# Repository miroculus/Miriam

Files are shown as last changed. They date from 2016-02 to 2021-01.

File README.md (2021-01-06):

Miriam
========

**🆕📻⚠️ IMPORTANT: A more updated repository which fixes several critical bugs is at https://github.com/strawlab/Miriam .**



Copyright Miroculus Inc.2016
Based on original work from Arduino (Sweden)

This documentation describes Open Hardware and is licensed under the CERN OHL v. 1.2.

Licensed under CERN OHL v.1.2

You may redistribute and modify this documentation under the terms of the [CERN OHL v.1.2.](http://ohwr.org/cernohl). This documentation is distributed WITHOUT ANY EXPRESS OR IMPLIED WARRANTY, INCLUDING OF MERCHANTABILITY, SATISFACTORY QUALITY AND FITNESS FOR A PARTICULAR PURPOSE. Please see the CERN OHL v.1.2 for applicable conditions

## Introduction

Miriam is an open-source instrument for isothermal amplification reactions. The assays Miriam was designed to execute are based on LAMP and Elisa protocols. Miriam is controlled with [Arduino](http://www.arduino.cc/) Mega and the production costs per instrument are blow 200USD.

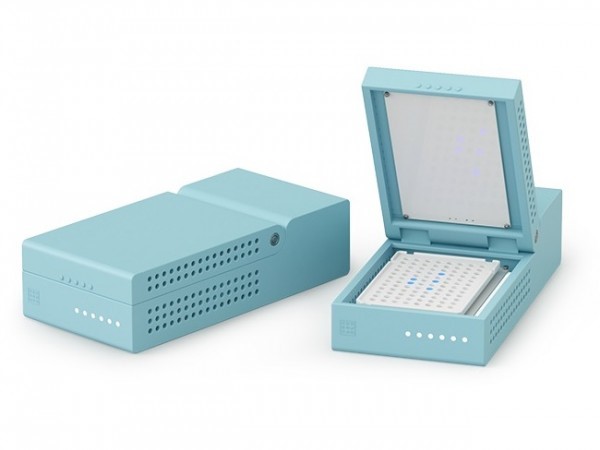
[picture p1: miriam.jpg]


The detection optics have been designed for [calcein dye](http://loopamp.eiken.co.jp/e/products/fluore/index.html). The selected LED is an angle SMD led with peak wavelength 461nm. The photodiode is an RGB photodiode most sensitive to green light. The optics also include an emission filter utilized in theatrical lighting.  The development and selection of components is further described in a [Master's thesis](http://lutpub.lut.fi/handle/10024/159386) done from miriam. 

In the performance testing of Miriam, the detection limit for DNA using LAMP as amplification platform has been 2amol in 10ul of sample (figure 1).

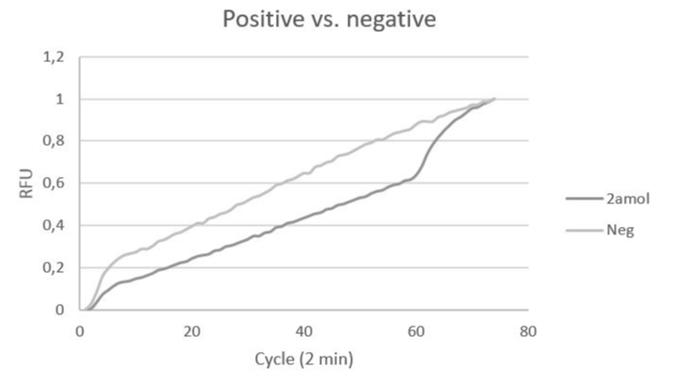
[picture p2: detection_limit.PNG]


**Figure 1.** LAMP reaction with 2amol DNA input, fluorescence measured every 2 minutes (y, Normalized signal and x, cycle (2 min).

For more information, you can contact us by completing the form [here](https://miroculus.com/#contact). You can also follow Miroculus on [twitter](https://twitter.com/miroculus) or like us on [facebook](https://www.facebook.com/miroculus).

To report a *bug* in the software or to request *a simple enhancement* go to the [issues](http://github.com/miroculus/Miriam/issues) section

If you're interested in modifying or extending the Miriam platform, we strongly suggest you to send us an email discussing your ideas. That way you can coordinate with our team and others, giving your work a higher chance of being integrated into the official release.

## Design

The optics of Miriam are designed to support calcein dye. Calcein emission and excitation spectra are represented in Figure 2.

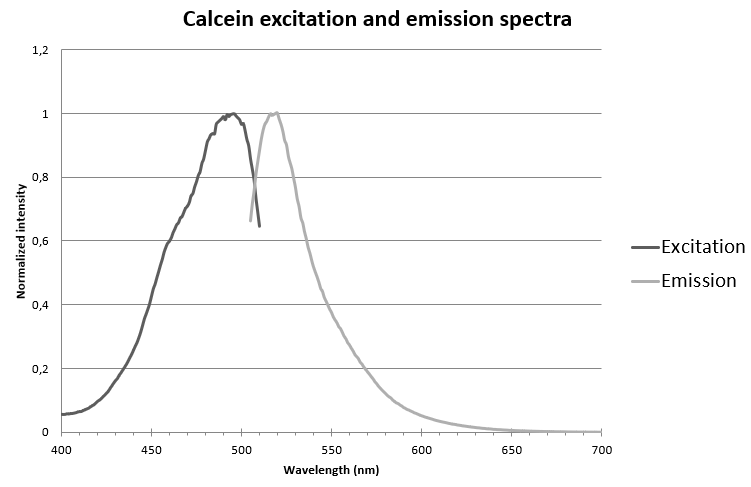
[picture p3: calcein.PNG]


**Figure 2.** Calcein normalized emission and excitation spectra.

The optical filter for blocking the excitation light has been purchased from a theatrical supply store and has the transmission spectra represented in Figure 3.

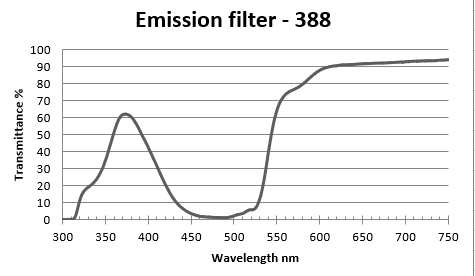
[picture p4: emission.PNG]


**Figure 3.** Emission filter transmission specter.

The middle heating board and the LED and PD arrangements have been designed to support 96-well plates with the following dimensions (figure 4).

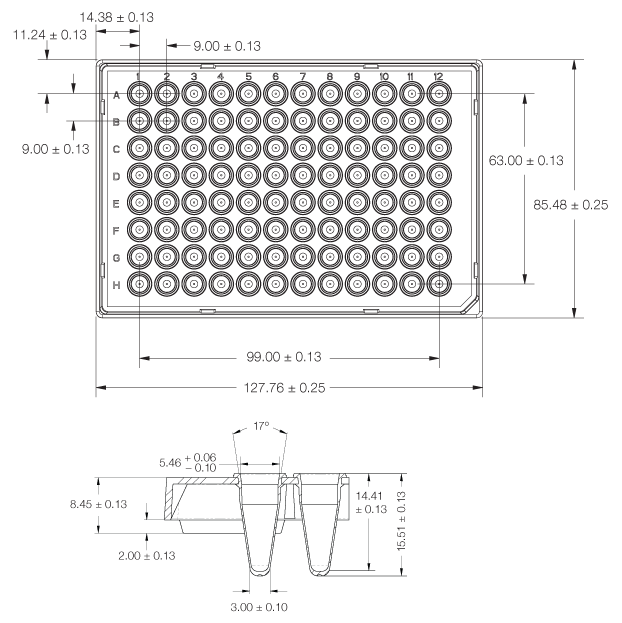
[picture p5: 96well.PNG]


**Figure 4.** 96-well plate dimensions supported by Miriam

To control the heating of Miriam there are two heater PCBs. They have been designed so that in the middle is a 10 kohm SMD thermistor and the heat is generated by current flowing through the copper traces. These traces have been designed to be so long and narrow that they create an internal resistance of few ohms. The traces are closer to each other in the edges because heat is measured from the middle and the edges of the PCB boards meet ambient air and they need to produce more heat. (Figure 5.)

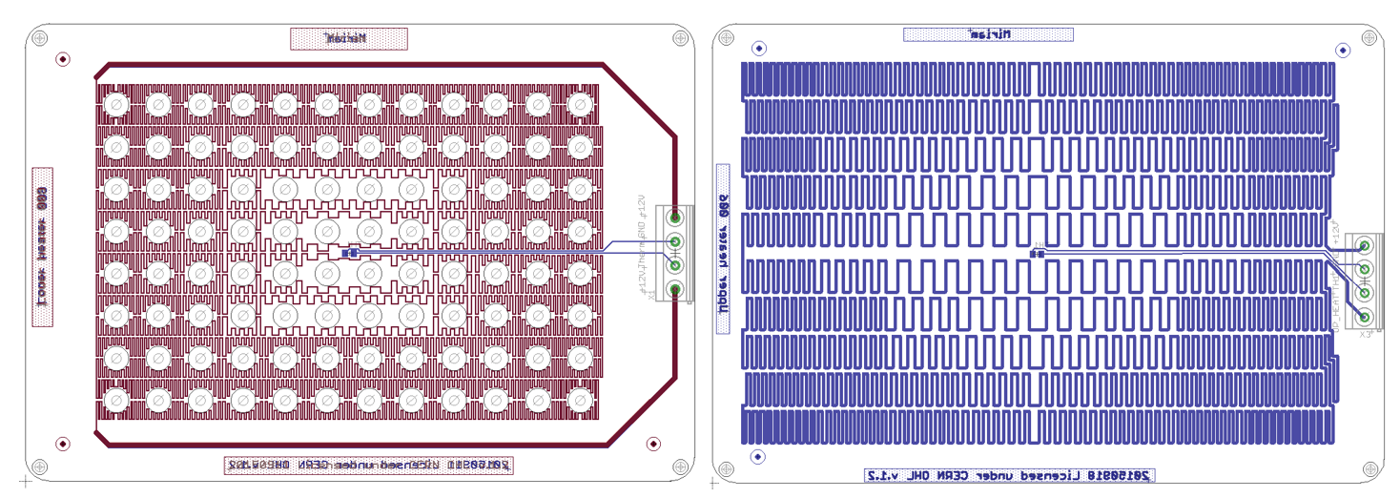
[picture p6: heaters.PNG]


**Figure 5.** Heating plates, heat is generated by trace resistance. Right: The middle heater creating the temperature required for amplification (58-68 degrees C). Left: The top heater keeping vapor from condensing to the lid, kept at 80 degrees C. 

The detection of fluorescence is done with 96 LEDs and 96 photodiodes creating LED and photodiode PCBs. The LED peak wavelength is 470 nm and photodiode is a green RGB photodiode. The measured voltage is amplified with an operational amplifier to 0-5 V that is then converted by Arduino’s 8-bit ADC to be a numerical value. (figure 6.)

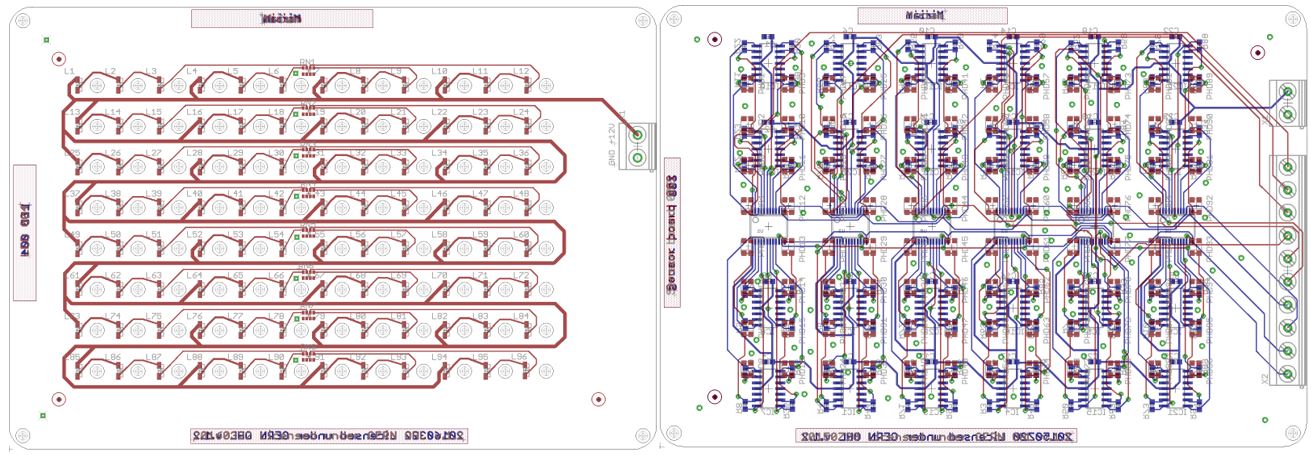
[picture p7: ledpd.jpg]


**Figure 6.** LED (left) and photodiode (right) PCBs.

All of these boards are controlled by a shield that is directly mounted to the Arduino mega board (figure 7). The shield contains three MOSFETs to control LED board and the two heater boards, the required components to read the heat from the thermistors as well as a WIFI chip. The WIFI chip makes it possible for Arduino to be connected to a local WIFI and this way communicate autonomously to a web service.

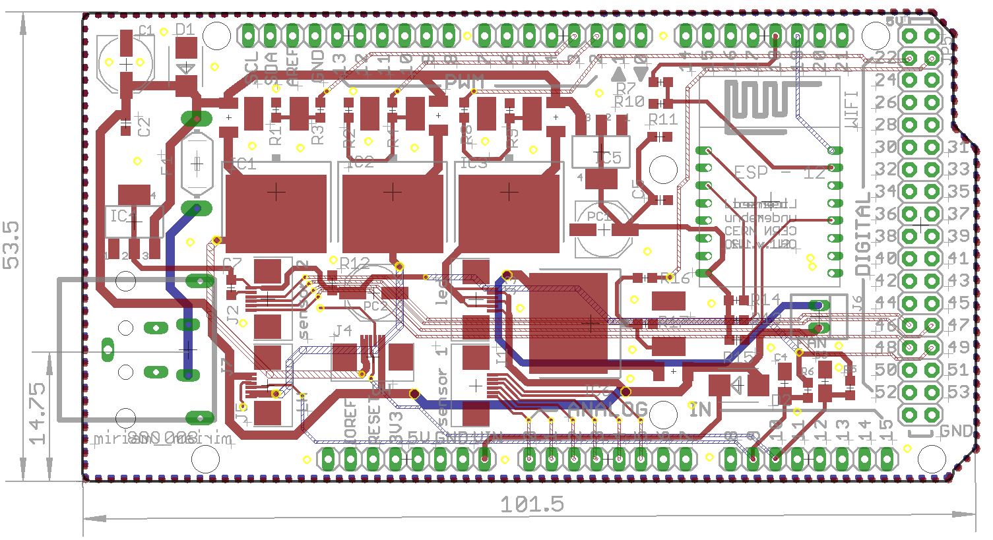
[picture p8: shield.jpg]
shield


**Figure 7.** The Arduino shield. The power connector is a 20-pin ATX connector that can be connected to a computer ATX power.

Installation
------------
3D print the printable parts under folder "3D model", sand them to make them align with each other. Assemble the boards as presented in the Figure 8. In the assembly cut with scissors the emission filter to fit between the LED and the sensor PCBs so that it aligns with the bolts.

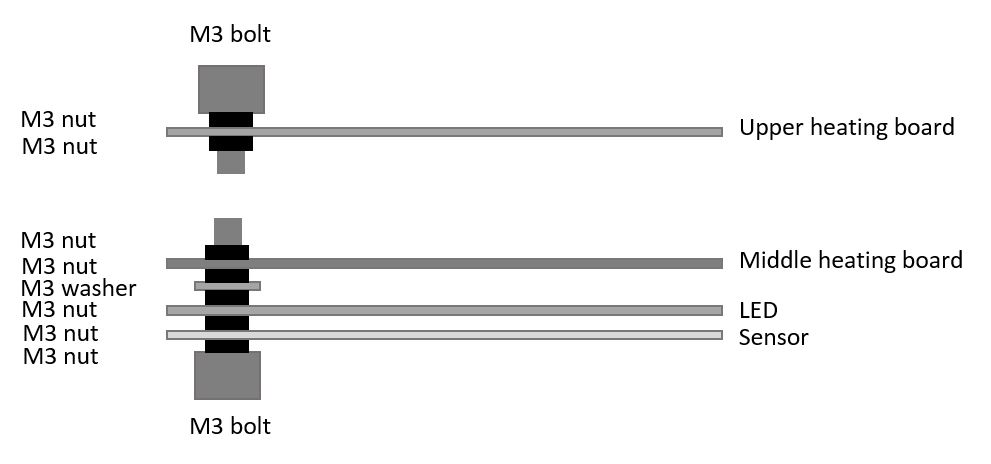
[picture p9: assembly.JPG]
screws


**Figure 8.** PCB board assembly information.

The screws are attached to the cover and the base with heat durable epoxy. 

Credits
--------
Miriam is an open source project, supported by Miroculus in collaboration with Arduino (Sweden). The team is led by Juho Terrijarvi.

Icon and image designed by Miroculus.

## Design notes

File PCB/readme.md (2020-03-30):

# PCBs

The PCBs have been drawn with Eagle software 7.3.0

PCB order details are in separate readme files in correct subfolders.

The Bills of material can be found under folder BOM. Datasheets of the main components are under folder Components.

Some of the component layouts can be found under Library folder that houses the Eagle .lbrs

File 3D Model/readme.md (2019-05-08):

# 3D printable parts

Miriam is composed of 3 pieces that can be 3D printed.

## base.stl

Base is where the mid heating and optic PCBs are located and where the plate to run the assay comes to. It also houses the Arduino Mega and its control shield in the back of the case. 

The outer dimensions of the base are 275 x 132 x 75 mm.

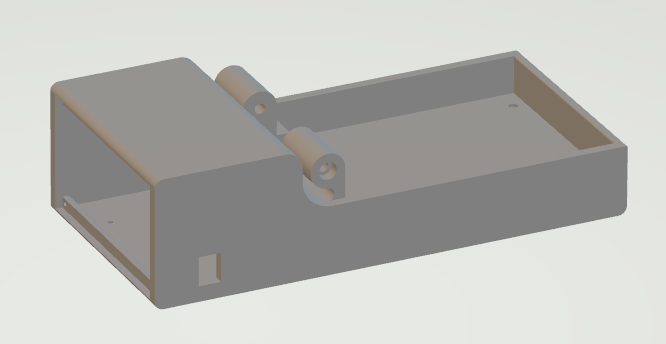
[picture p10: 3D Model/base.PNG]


## upper.stl 

This is the cover of the case that houses the upper heating board. The outer dimensions are 191 x 132 x 35 mm.

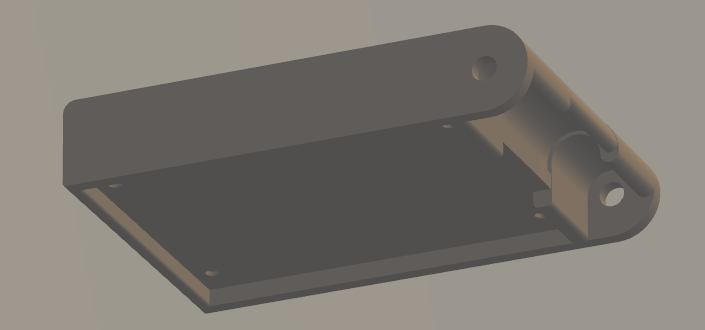
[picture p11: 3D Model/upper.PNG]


## cover.stl

Cover is meant to hide the Arduino mega and shield in the back of the case. The dimensions are 6 x 120 x 67 mm.

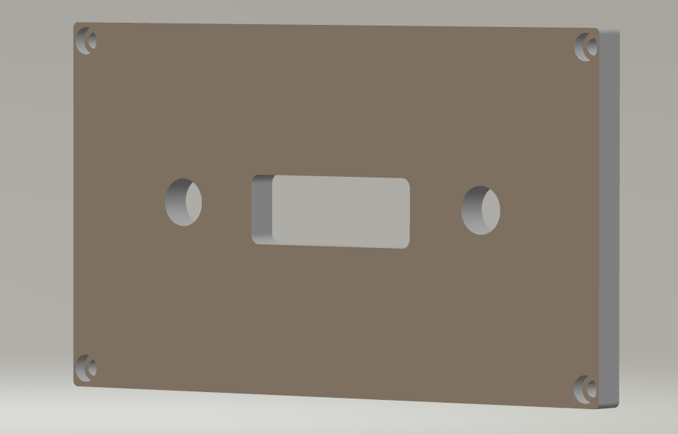
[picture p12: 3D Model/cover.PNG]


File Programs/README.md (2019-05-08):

Miriam SW/FW
========

(c) 2016 Juho Terrijarvi juho@miroculus.com, Miroculus Inc.

(c) 2014 Juanjo Tara j.tara@arduino.cc, Arduino Verkstad AB (For FWs)

These programs are free software: you can redistribute them and/or modify them under the terms of the GNU General Public License as published by the Free Software Foundation, either version 3 of the License, or (at your option) any later version.

These programs are distributed in the hope that they will be useful, but WITHOUT ANY WARRANTY; without even the implied warranty of MERCHANTABILITY or FITNESS FOR A PARTICULAR PURPOSE.  See the GNU General Public License for more details.

You should have received a copy of the GNU General Public License along with this program.  If not, see <http://www.gnu.org/licenses/>.

## Programs

Firmware is written with [Arduino IDE](https://www.arduino.cc/en/main/software) and the software with Visual Studio 2015 open community using C#.

* Serial_003 is meant for communication between computer and Miriam via USB cable and string messages
* Wifi_003 is for interaction between controller and Miriam over the same wifi network
* Wifi_004 webservice controls Miriam

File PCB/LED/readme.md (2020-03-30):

# LED_005

- material: FR4
- Single sided assembly
- 1oz copper
- 1.6 mm thick
- Leadfree HAL
- Black soldermask
- White silkscreen

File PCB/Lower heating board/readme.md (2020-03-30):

# LH_010

- material aluminum
- 2 layer
- single sided assembly
- 1oz copper
- 1.6 mm thick
- Leadfree HAL
- Black soldermask
- White silkscreen

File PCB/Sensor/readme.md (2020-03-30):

# Sensor_002

- material FR4
- 2 layer
- double sided assembly
- 1oz copper
- 1.6 mm thick
- Leadfree HAL
- Black soldermask
- White silkscreen

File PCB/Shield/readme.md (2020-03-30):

# shield_008

- material FR4
- 4 layers
- 1oz copper
- 1.6 mm thick
- Leadfree HAL
- Black soldermask
- White silkscreen
- Pay attention to milling layer GML
- One sided assembly

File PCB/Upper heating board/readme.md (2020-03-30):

# UH_007

- 2 layer PCB
- One sided assembly
- material FR4
- 1oz copper
- 1.6 mm thick
- Leadfree HAL
- Black soldermask
- White silkscreen

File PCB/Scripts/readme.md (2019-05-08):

# Scripts

This folder has the outer dimensions of each PCB. Script template.csv is an example script to draw the traces for the heating boards. It was easiest to calculate the lengths of each wire in Excel.

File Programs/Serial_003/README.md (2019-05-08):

Serial_003
========

This SW / FW combination is meant for serial communication between a computer and Miriam. Miriam is connected with a USB cable to the controlling computer and messaging between the two happen via string messages over RX/TX protocol.
- SW 'R' (read assay) - FW 'A1,A2,A3...E12'
- SW 'i' (info) - FW 'outputMiddle, outputUpper, temperatureMiddle, temperatureUpper, temperatureMiddleC, temperatureUpperC'
- SW 'U param' (upper wanted temperature, i.e. U 80) - FW 'temperatureUpperSet'
- SW 'M param' (middle wanted temperature, i.e. M 63) - FW 'temperatureMiddleSet'
- SW 'C' (cancel, turn off the heat) - FW 'Cancel'

Once the temperature has been set, the actual temperature needs to be refreshed by clicking 'Ask heat'. The assay, once started, can always be turned off simply by closing the program. The assay results are saved to the desktop in a .csv file.

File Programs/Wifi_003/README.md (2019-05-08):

Wifi_003
========

This SW / FW combination is meant for communication over the same WIFI connection between a computer and Miriam. Miriam is first connected with a USB cable to the controlling computer and the WIFI details are given to Miriam and the IP address when connected read. Messaging between the two happen via string messages in http format.
- SW 'R' (read assay) - FW 'A1,A2,A3...E12'
- SW 'i' (info) - FW 'outputMiddle, outputUpper, temperatureMiddle, temperatureUpper, temperatureMiddleC, temperatureUpperC'
- SW 'U param' (upper wanted temperature, i.e. U 80) - FW 'temperatureUpperSet'
- SW 'M param' (middle wanted temperature, i.e. M 63) - FW 'temperatureMiddleSet'
- SW 'C' (cancel, turn off the heat) - FW 'Cancel'

Once the temperature has been set, the actual temperature needs to be refreshed by clicking 'Ask heat'. The assay, once started, can always be turned off simply by closing the program. The assay results are saved to the desktop in a .csv file.

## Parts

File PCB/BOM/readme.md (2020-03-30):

# Components

Components required for the PCB assembly are listed in the BOMs. Main components contain a link to the component. Datasheets can be found under ./Components.

The emission filter is purchased from a Swedish theatrical supply store. The transmission spectrum of the [GAM-388](http://shop.hofmann.se/GAM_Orange_gold_rush_filter?id=388-GAM#.VaYDufktM9s) filter is represented in the main readme. To even out the distribution of heat an [elastic heat pressure surface](http://catalog.cshyde.com/item/all-categories/solid-silicone-thermally-conductive-/71-tcd-60d-0625) can be used between the 96-well plate and the upper heating board.

List of the components can also be found from [joint bom](List of components required can be found: https://docs.google.com/spreadsheets/d/1FHOCzn1yYIiR1e6U7Qw9gCIf-KbuHXV_sOKSGwqRR3c/edit?usp=sharing) where also a possible power supply is listed.

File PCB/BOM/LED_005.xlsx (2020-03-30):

PCB: | LED_003
part | pcs/pcb | Value | Package | Description | Remark | Link
RN1,RN2,RN3,RN4,RN5,RN6,RN7,RN8 | 8 | 181 | CAY16 | Array Chip Resistor | 4R-NCAY16 | http://www.digikey.hk/product-detail/en/bourns-inc/CAT16-181J4LF/CAT16-181J4LFCT-ND/3592895
FD1,FD2,FD3 | 3 | FIDUCIALMOUNT | FIDUCIA-MOUNT | FIDUCIALMOUNT
L1,L2,L3,L4,L5,L6,L7,L8,L9,L10,L11,L12,L13,L14,L15,L16,L17,L18,L19,L20,L21,L22,L23,L24,L25,L26,L27,L28,L29,L30,L31,L32,L33,L34,L35,L36,L37,L38,L39,L40,L41,L42,L43,L44,L45,L46,L47,L48,L49,L50,L51,L52,L53,L54,L55,L56,L57,L58,L59,L60,L61,L62,L63,L64,L65,L66,L67,L68,L69,L70,L71,L72,L73,L74,L75,L76,L77,L78,L79,L80,L81,L82,L83,L84,L85,L86,L87,L88,L89,L90,L91,L92,L93,L94,L95,L96 | 96 | KA-2810AQBS-G | LED_0.2 | LED_0.2 | LED | http://www.newark.com/kingbright/ka-2810aqbs-g/led-blue-2-8-x-0-8mm-300mcd-465nm/dp/28W1790?ost=KA-2810AQBS-G
J1 | 1 |  | 68710614522 | WE-FPC 0.5mm SMT ZIF Horizontal Bottom Contact, 6 Pins=>Code : Con_FPC_ZIF_0.50_68710614522 |  | https://www.digikey.fi/product-detail/en/wurth-electronics-inc/68710614522/732-2010-1-ND/2060634

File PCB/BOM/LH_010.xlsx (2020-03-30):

PCB: | LH_010
part | pcs/pcb | Value | Package | Description | Remark
J1 | 1 |  | 68710614522 | WE-FPC 0.5mm SMT ZIF Horizontal Bottom Contact, 6 Pins=>Code : Con_FPC_ZIF_0.50_68710614522 |  | https://www.digikey.fi/product-detail/en/wurth-electronics-inc/68710614522/732-2010-1-ND/2060634
TH1 | 1 | 10K | THERMISTOR_SMD_0603 | THERMISTOR_SMD_0603 | NTC

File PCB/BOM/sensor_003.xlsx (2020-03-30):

PCB: | sensor_002
part | pcs/pcb | Value | Package | Description | Remark | Link
C1,C2,C3,C4,C5,C6,C7,C8,C9,C10,C11,C12,C13,C14,C15,C16,C17,C18,C19,C20,C21,C22,C23,C25 | 24 | 100nF | C0603 | C-EUC0603 | CAPACITOR, European symbol
R1,R2,R3,R4,R5,R7,R8,R9,R10,R11,R12,R13,R14,R15,R16,R17,R18,R19,R20,R21,R22,R23,R24,R25,R26,R27,R28,R29,R30,R31,R32,R33,R34,R35,R36,R37,R38,R39,R40,R41,R42,R43,R44,R45,R46,R47,R48,R49,R50,R51,R52,R53,R54,R55,R56,R57,R58,R59,R60,R61,R62,R63,R64,R65,R66,R67,R68,R69,R70,R71,R72,R73,R74,R75,R76,R77,R78,R79,R80,R81,R82,R83,R84,R85,R86,R87,R88,R89,R90,R91,R92,R93,R94,R95,R96,R97 | 96 | 3.9Mohm | R0603 | R-EU_R0603 | RESISTOR, European symbol
U1,U2,U3,U4,U5,U6 | 6 | 74HC4067 | SSOP24 | MUX-1X16 | 1x16 Channel Analog Multiplexer/Demultiplexer [Part No.] | http://www2.mouser.com/ProductDetail/Texas-Instruments/CD74HC4067SM96G4/
PHD1,PHD2,PHD3,PHD4,PHD5,PHD6,PHD7,PHD8,PHD9,PHD10,PHD11,PHD12,PHD13,PHD14,PHD15,PHD16,PHD17,PHD18,PHD19,PHD20,PHD21,PHD22,PHD23,PHD24,PHD25,PHD26,PHD27,PHD28,PHD29,PHD30,PHD31,PHD32,PHD33,PHD34,PHD35,PHD36,PHD37,PHD38,PHD39,PHD40,PHD41,PHD42,PHD43,PHD44,PHD45,PHD46,PHD47,PHD48,PHD49,PHD50,PHD51,PHD52,PHD53,PHD54,PHD55,PHD56,PHD57,PHD58,PHD59,PHD60,PHD61,PHD62,PHD63,PHD64,PHD65,PHD66,PHD67,PHD68,PHD69,PHD70,PHD71,PHD72,PHD73,PHD74,PHD75,PHD76,PHD77,PHD78,PHD79,PHD80,PHD81,PHD82,PHD83,PHD84,PHD85,PHD86,PHD87,PHD88,PHD89,PHD90,PHD91,PHD92,PHD93,PHD94,PHD95,PHD96 | 96 | CLS15-22C/L213G/TR8 | PD_0.2 | PD_0.2 | Photodiode | http://www2.mouser.com/ProductDetail/Everlight/CLS15-22C-L213G-TR8/
FD1,FD2,FD3,FD4,FD5,FD6 | 6 | FIDUCIALMOUNT | FIDUCIALMOUNT | FIDUCIA-MOUNT
IC1,IC2,IC3,IC4,IC5,IC6,IC7,IC8,IC9,IC10,IC11,IC12,IC13,IC14,IC15,IC16,IC17,IC18,IC19,IC20,IC21,IC22,IC23,IC24 | 24 | LMV324 | SO14 |  | OP AMP | http://www2.mouser.com/ProductDetail/STMicroelectronics/LMV324LIDT/?qs=sGAEpiMZZMtCHixnSjNA6A1cCp3RWdULNBEJMAycdn8%3d
J1, J2 | 2 |  | 68710614522 | WE-FPC 0.5mm SMT ZIF Horizontal Bottom Contact, 6 Pins=>Code : Con_FPC_ZIF_0.50_68710614522 |  | https://www.digikey.fi/product-detail/en/wurth-electronics-inc/68710614522/732-2010-1-ND/2060634

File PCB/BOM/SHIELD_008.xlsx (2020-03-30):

PCB: | SHIELD_008
part | pcs/pcb | Value | Package | Description | Remark | Link
R7 | 1 | 1.69k | R0603 | RESISTOR, European symbol
R3, R4, R8, R16 | 4 | 100R | R0603 | RESISTOR, European symbol
C2, C5, C7 | 3 | 100n | C0603 | CAPACITOR, European symbol
R1, R2, R5, R6, R9, R13, R14, R15, R17 | 9 | 10K | R0603 | RESISTOR, European symbol
C3, C4 | 2 | 10u | A/3216-18R | POLARIZED CAPACITOR, European symbol |  | http://www2.mouser.com/ProductDetail/AVX/TPSA106K010R0900/?qs=YMBIwoNQYdV0MtGvKI9mmw%3D%3D
JP7 | 1 | 10x1F-H8.5 | 1X10 | PIN HEADER
JP5 | 1 | 18x2F-H8.5 | 2X18 | PIN HEADER
J6 | 1 | 22-23-2021 | 22-23-2021 | .100 (2.54mm) Center Header - 2 Pin"
R10 | 1 | 3.3k | R0603 | RESISTOR, European symbol
R11, R12 | 2 | 4.12k | R0603 | RESISTOR, European symbol
C1, PC1, PC2 | 3 | 47u | PANASONIC_D | POLARIZED CAPACITOR, European symbol |  | http://www.digikey.com/product-search/en?KeyWords=493-2086-1-ND&WT.z_header=search_go
JP1, JP2, JP3, JP4, JP6 | 5 | 8x1F-H8.5 | 1X08 | PIN HEADER
IC1, IC2, IC3, IC6 | 4 | FDB8880 | FDB8880 | FDB8880 N-Channel PowerTrench MOSFET |  | http://www2.mouser.com/ProductDetail/Fairchild-Semiconductor/FDB8880/
WIFI | 1 | ESP12 | ESP12 | ESP8266 Wifi module 12 |  | https://www.amazon.com/gp/aw/d/B00RJJHWLA/ref=ya_aw_od_pi?ie=UTF8&psc=1
D1, D2 | 2 | M7 | SMB | DIODE |  | http://www.digikey.com/product-detail/en/S1AB-13-F/S1AB-FDICT-ND/755488
F1 | 1 | MF-R1100 | LITTLEFUSE | LITTLEFUSE |  | http://www.digikey.com/product-search/en?KeyWords=MF-R1100-ND&WT.z_header=search_go
IC4 | 1 | NCV1117ST50T3GOSCT-ND | SOT223 | Adjustable Output Low Dropout Voltage Regulator 800 mA |  | http://www.digikey.com/product-detail/en/NCV1117ST50T3G/NCV1117ST50T3GOSCT-ND/1967231
IC5 | 1 | NCV1117ST33T3GOSCT-ND |  | Adjustable Output Low Dropout Voltage Regulator 800 mA |  | http://www.digikey.com/product-detail/en/NCV1117ST33T3G/NCV1117ST33T3GOSCT-ND/2705186
D3, D4, D5, D6 | 4 | RGL34A | DO-213AA_DIODE | RGL34A thru RGL34K |  | http://www.digikey.com/product-search/en?keywords=RGL34G-E3%2F98GICT-ND
J7 | 1 | KPJX-4S-S | KPJX-4S-S | 4 _Power_ Position Circular Connector Jack, Female Sockets Solder |  | https://www.digikey.fi/product-detail/en/kycon-inc/KPJX-4S-S/2092-KPJX-4S-S-ND/9990088
J1, J2, J3, J4, J5 | 5 |  | 68710614522 | WE-FPC 0.5mm SMT ZIF Horizontal Bottom Contact, 6 Pins=>Code : Con_FPC_ZIF_0.50_68710614522 |  | https://www.digikey.fi/product-detail/en/wurth-electronics-inc/68710614522/732-2010-1-ND/2060634

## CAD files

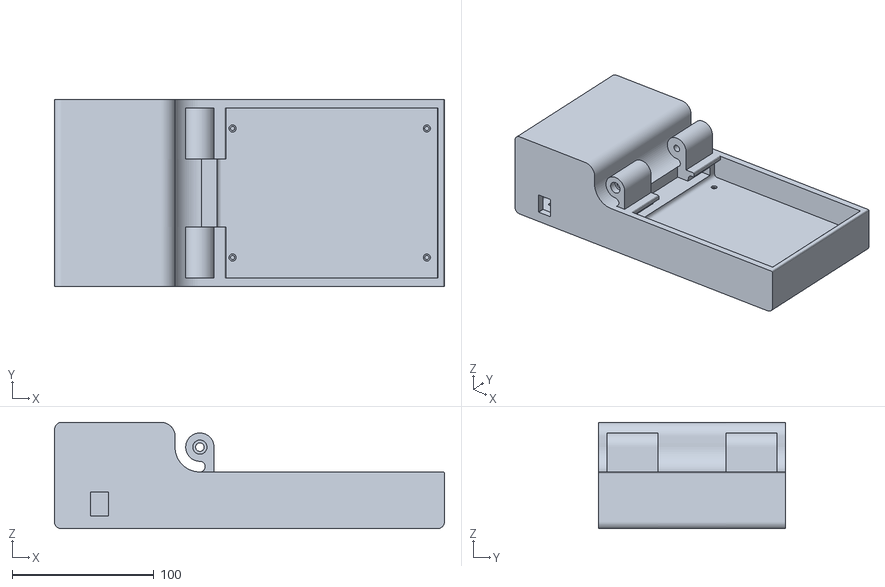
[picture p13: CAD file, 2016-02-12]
3D Model/base.stl
275.0 x 132.0 x 75.0

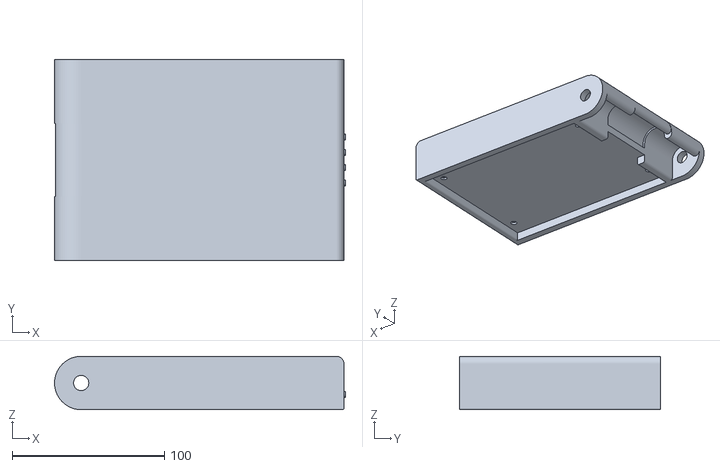
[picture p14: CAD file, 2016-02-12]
3D Model/upper.stl
191.0 x 132.0 x 35.0

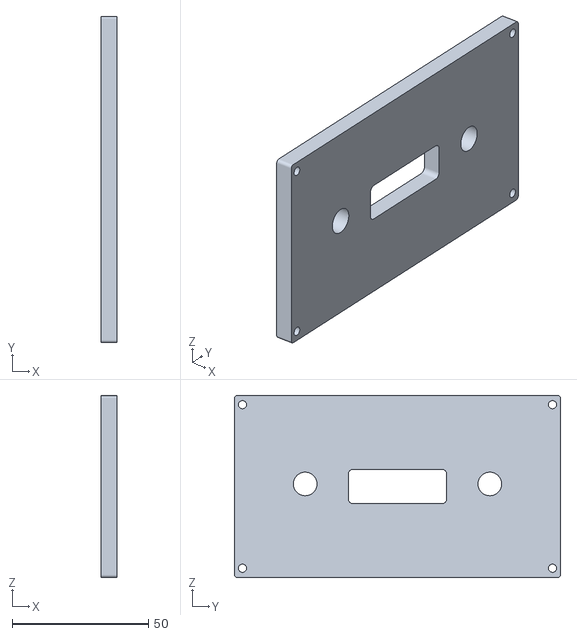
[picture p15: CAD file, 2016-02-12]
3D Model/cover.stl
6.00 x 119.8 x 66.8

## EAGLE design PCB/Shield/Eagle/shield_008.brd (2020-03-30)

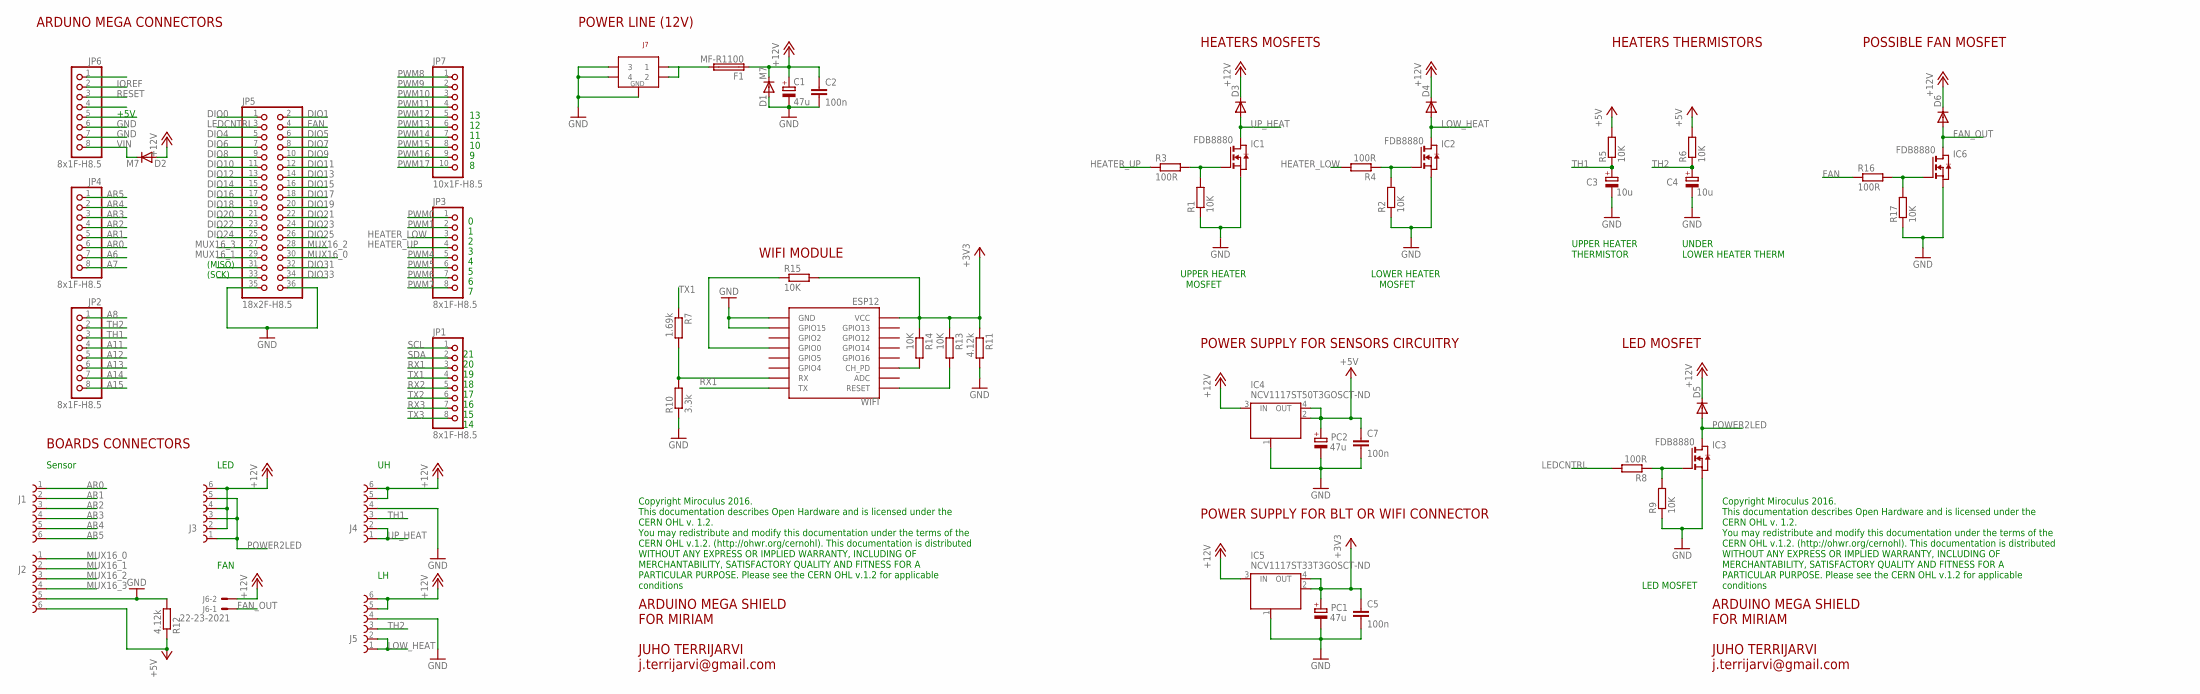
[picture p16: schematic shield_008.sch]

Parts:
C1: 47u; PANASONIC_D
C2, C5, C7: 100n; C0603
C3, C4: 10u; A/3216-18R
D1, D2: M7; SMB
D3, D4, D5, D6: RGL34A; DO-213AA_DIODE
F1: MF-R1100; LITTLEFUSE; FARNELL 1652183
IC1, IC2, IC3, IC6: FDB8880
IC4: NCV1117ST50T3GOSCT-ND; SOT223
IC5: NCV1117ST33T3GOSCT-ND; SOT223
J1, J2, J3, J4, J5: 68710614522
J6: 22-23-2021
J7: KPJX-4S-S
JP1, JP2, JP3, JP4, JP6: 8x1F-H8.5; 1X08
JP5: 18x2F-H8.5; 2X18
JP7: 10x1F-H8.5; 1X10
PC1, PC2: 47u; PANASONIC_D
R1, R2, R5, R6, R9, R13, R14, R15, R17: 10K; R0603
R3, R4, R8, R16: 100R; R0603
R7: 1.69k; R0603
R10: 3.3k; R0603
R11, R12: 4.12k; R0603
WIFI: ESP12

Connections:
+3V3: C5.1, IC5.2 (OUT), IC5.4 (OUT), PC1.+, R11.1, R13.1, R14.1, R15.2, WIFI.VCC
+5V: C7.1, IC4.2 (OUT), IC4.4 (OUT), J2.6, PC2.+, R5.2, R6.2, R12.1
+12V: C1.+, C2.1, D1.C, D2.A, D3.P$2 (C), D4.P$2 (C), D5.P$2 (C), D6.P$2 (C), F1.1, IC4.3 (IN), IC5.3 (IN), J3.2, J3.4, J3.6, J4.5, J4.6, J5.5, J5.6, J6.2
A6: JP4.7
A7: JP4.8
A8: JP2.1
A11: JP2.4
A12: JP2.5
A13: JP2.6
A14: JP2.7
A15: JP2.8
AR0: J1.1, JP4.6
AR1: J1.2, JP4.5
AR2: J1.3, JP4.4
AR3: J1.4, JP4.3
AR4: J1.5, JP4.2
AR5: J1.6, JP4.1
DIO0: JP5.1
DIO1: JP5.2
DIO4: JP5.5
DIO5: JP5.6
DIO6: JP5.7
DIO7: JP5.8
DIO8: JP5.9
DIO9: JP5.10
DIO10: JP5.11
DIO11: JP5.12
DIO12: JP5.13
DIO13: JP5.14
DIO14: JP5.15
DIO15: JP5.16
DIO16: JP5.17
DIO17: JP5.18
DIO18: JP5.19
DIO19: JP5.20
DIO20: JP5.21
DIO21: JP5.22
DIO22: JP5.23
DIO23: JP5.24
DIO24: JP5.25
DIO25: JP5.26
DIO30: JP5.31
DIO31: JP5.32
DIO32: JP5.33
DIO33: JP5.34
FAN: JP5.4, R16.1
FAN_OUT: D6.P$1 (A), IC6.2 (D), J6.1
GND: C1.-, C2.2, C3.-, C4.-, C5.2, C7.2, D1.A, IC1.3 (S), IC2.3 (S), IC3.3 (S), IC4.1 (GND/ADJ), IC5.1 (GND/ADJ), IC6.3 (S), J2.5, J4.4, J5.4, J7.P$3 (3), J7.P$4 (4), J7.P$5 (G), J7.P$6 (G), J7.P$7 (G), JP5.35, JP5.36, JP6.6, JP6.7, PC1.-, PC2.-, R1.1, R2.1, R9.1, R10.1, R11.2, R12.2, R17.1, WIFI.GND, WIFI.GPIO15
HEATER_LOW: JP3.3, R4.2
HEATER_UP: JP3.4, R3.1
IOREF: JP6.2
LEDCNTRL: JP5.3, R8.2
LOW_HEAT: D4.P$1 (A), IC2.2 (D), J5.1, J5.2
MUX16_0: J2.1, JP5.30
MUX16_1: J2.2, JP5.29
MUX16_2: J2.3, JP5.28
MUX16_3: J2.4, JP5.27
unnamed: IC3.1 (G), R8.1, R9.2
unnamed: R7.2, R10.2, WIFI.RX
unnamed: R13.2, WIFI.RESET
unnamed: R14.2, WIFI.CH_PD
unnamed: R15.1, WIFI.GPIO0
unnamed: F1.2, J7.P$1 (1), J7.P$2 (2)
unnamed: IC6.1 (G), R16.2, R17.2
unnamed: IC1.1 (G), R1.2, R3.2
unnamed: IC2.1 (G), R2.2, R4.1
POWER2LED: D5.P$1 (A), IC3.2 (D), J3.1, J3.3, J3.5
PWM0: JP3.1
PWM1: JP3.2
PWM4: JP3.5
PWM5: JP3.6
PWM6: JP3.7
PWM7: JP3.8
PWM8: JP7.1
PWM9: JP7.2
PWM10: JP7.3
PWM11: JP7.4
PWM12: JP7.5
PWM13: JP7.6
PWM14: JP7.7
PWM15: JP7.8
PWM16: JP7.9
PWM17: JP7.10
RESET: JP6.3
RX1: JP1.3, WIFI.TX
RX2: JP1.5
RX3: JP1.7
SCL: JP1.1
SDA: JP1.2
TH1: C3.+, J4.3, JP2.3, R5.1
TH2: C4.+, J5.3, JP2.2, R6.1
TX1: JP1.4, R7.1
TX2: JP1.6
TX3: JP1.8
UP_HEAT: D3.P$1 (A), IC1.2 (D), J4.1, J4.2
VIN: D2.C, JP6.8

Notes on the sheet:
(SCK)
(MISO)
ARDUNO MEGA CONNECTORS
ARDUINO MEGA SHIELD FOR MIRIAM JUHO TERRIJARVI j.terrijarvi@gmail.com
POWER LINE (12V)
BOARDS CONNECTORS
HEATERS MOSFETS
HEATERS THERMISTORS
UPPER HEATER THERMISTOR
UNDER LOWER HEATER THERM
UPPER HEATER MOSFET
LOWER HEATER MOSFET
WIFI MODULE
+5V
POWER SUPPLY FOR SENSORS CIRCUITRY
LED MOSFET
POWER SUPPLY FOR BLT OR WIFI CONNECTOR
Copyright Miroculus 2016. This documentation describes Open Hardware and is licensed under the CERN OHL v. 1.2. You may redistribute and modify this documentation under the terms of the CERN OHL v.1.2. (http://ohwr.org/cernohl). This documentation is distributed WITHOUT ANY EXPRESS OR IMPLIED WARRA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
Sensor
LED
POSSIBLE FAN MOSFET
FAN

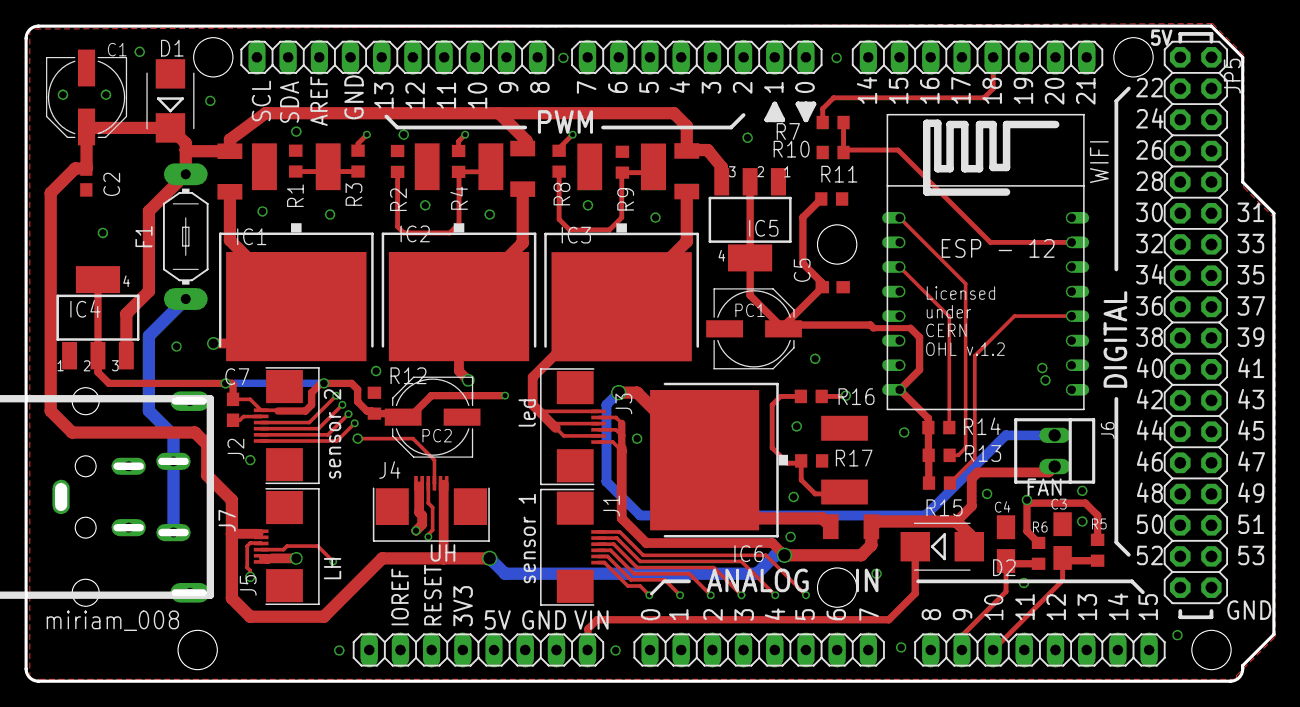
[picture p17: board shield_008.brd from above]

Board: 4 copper layers, 101.6 x 53.3 mm, 53 parts (0 on the bottom side), 36 nets.

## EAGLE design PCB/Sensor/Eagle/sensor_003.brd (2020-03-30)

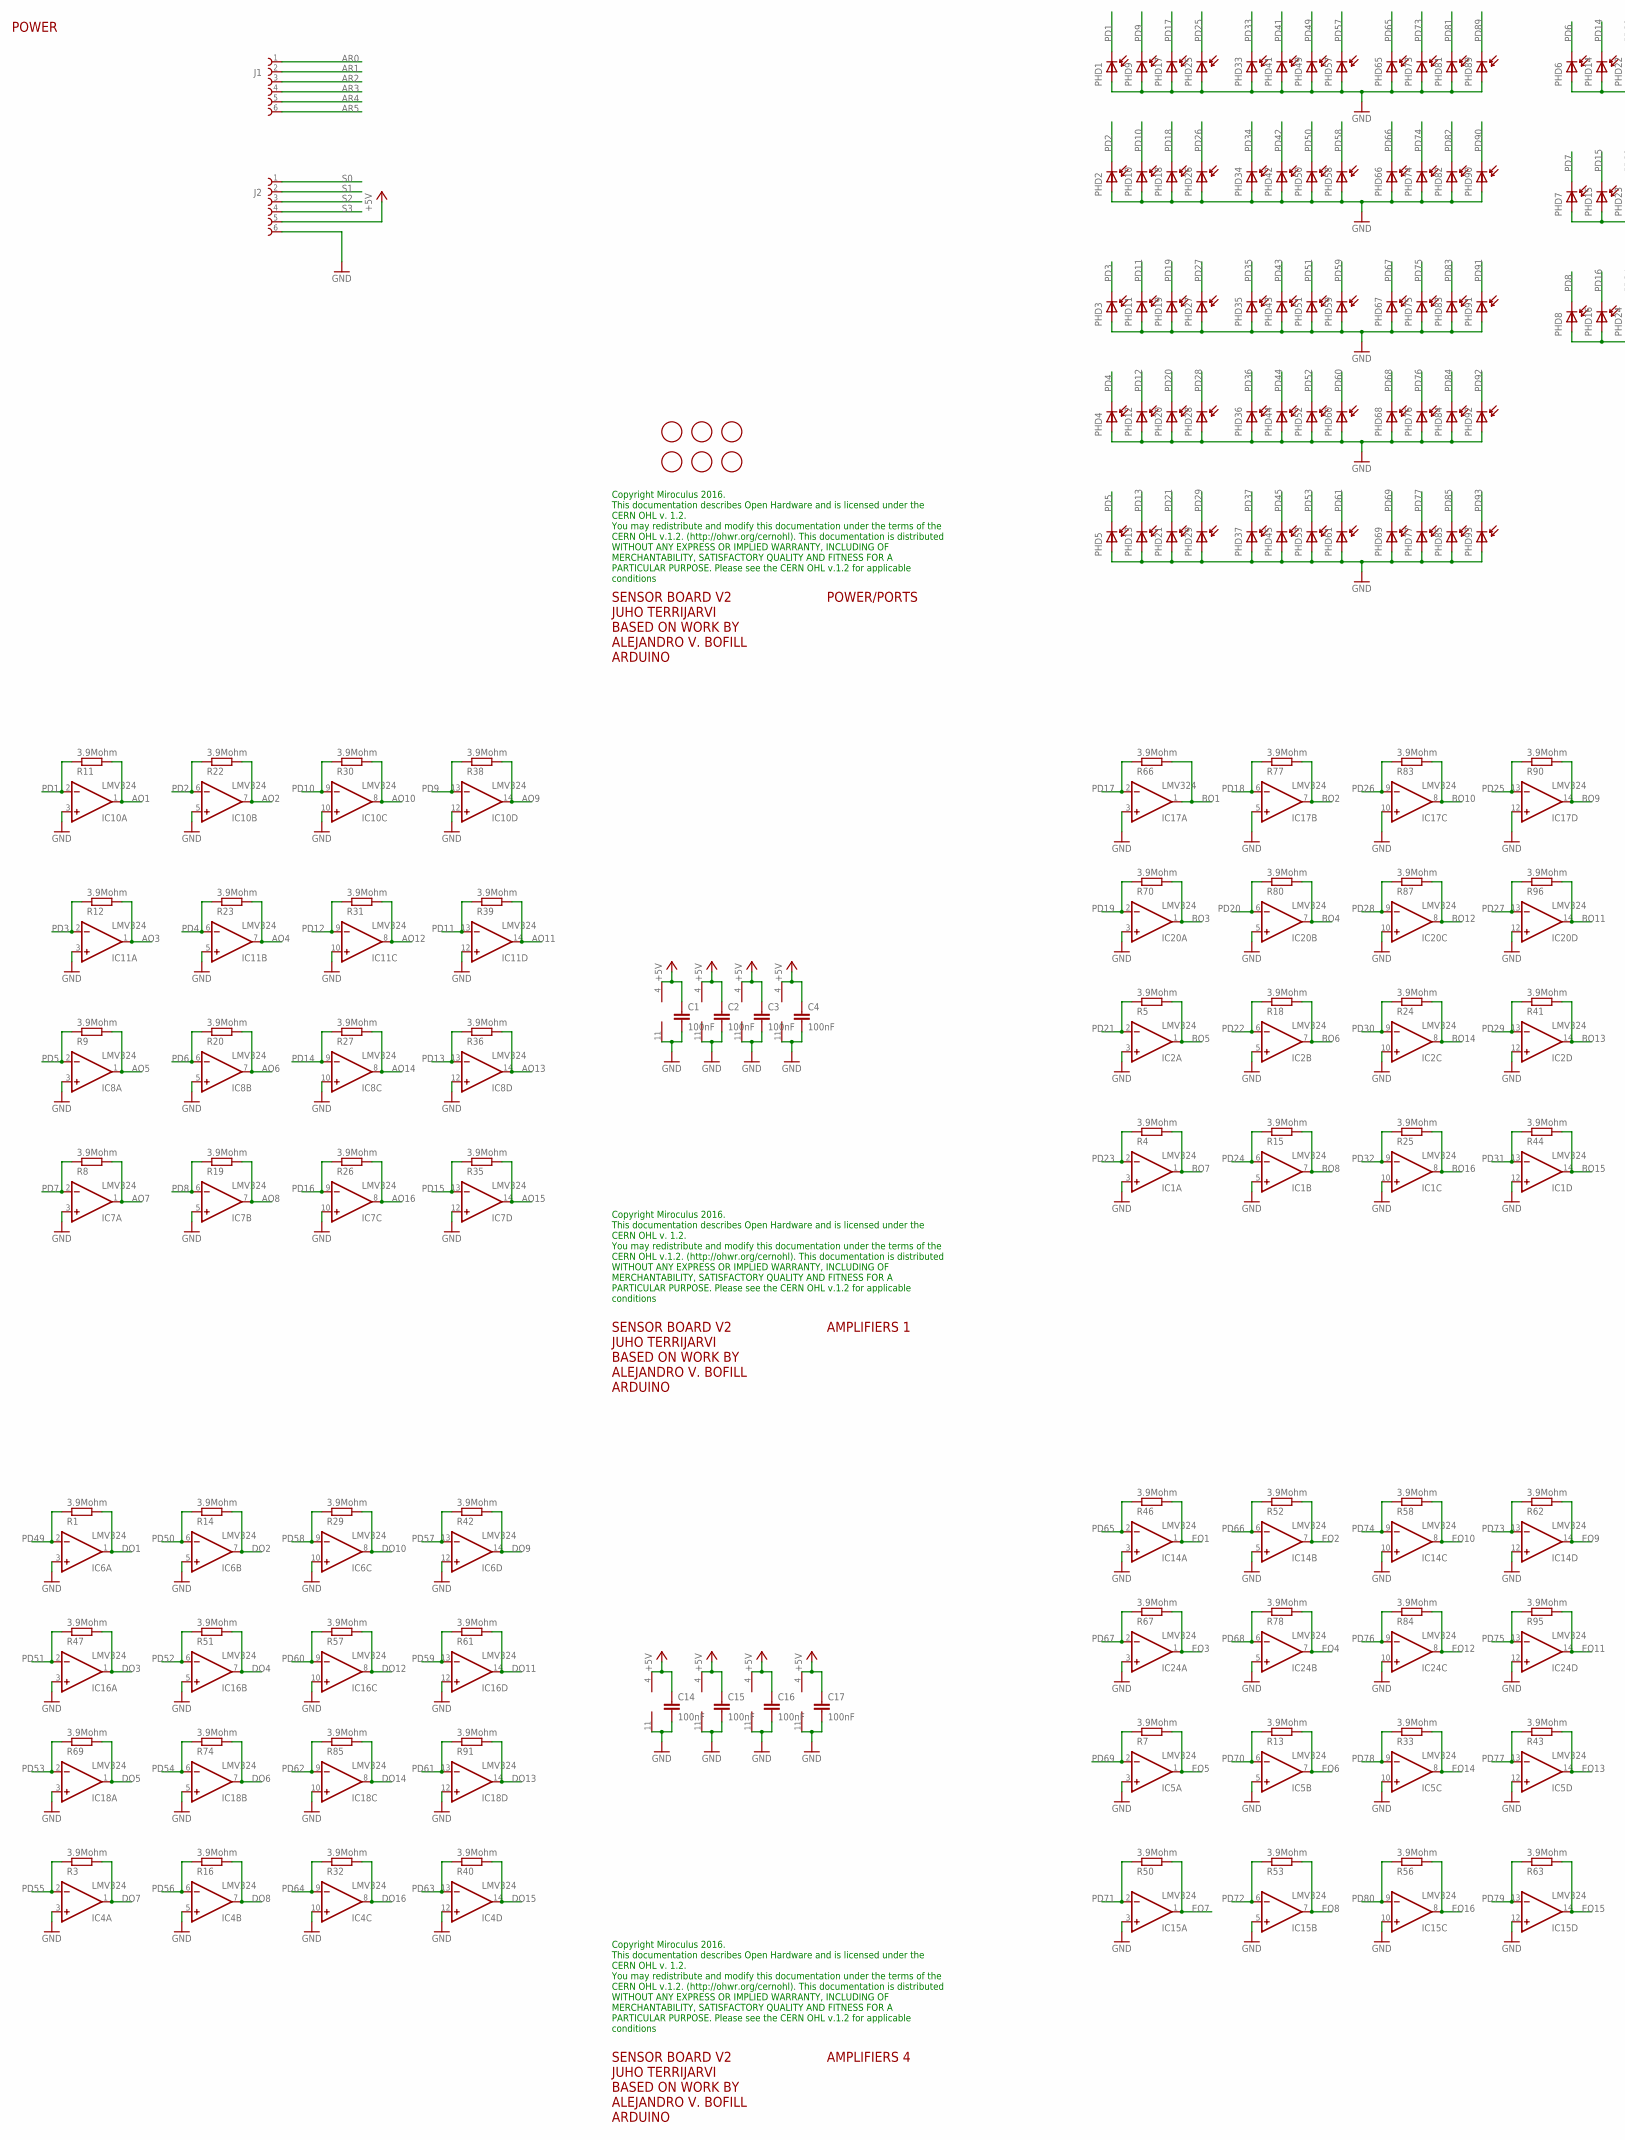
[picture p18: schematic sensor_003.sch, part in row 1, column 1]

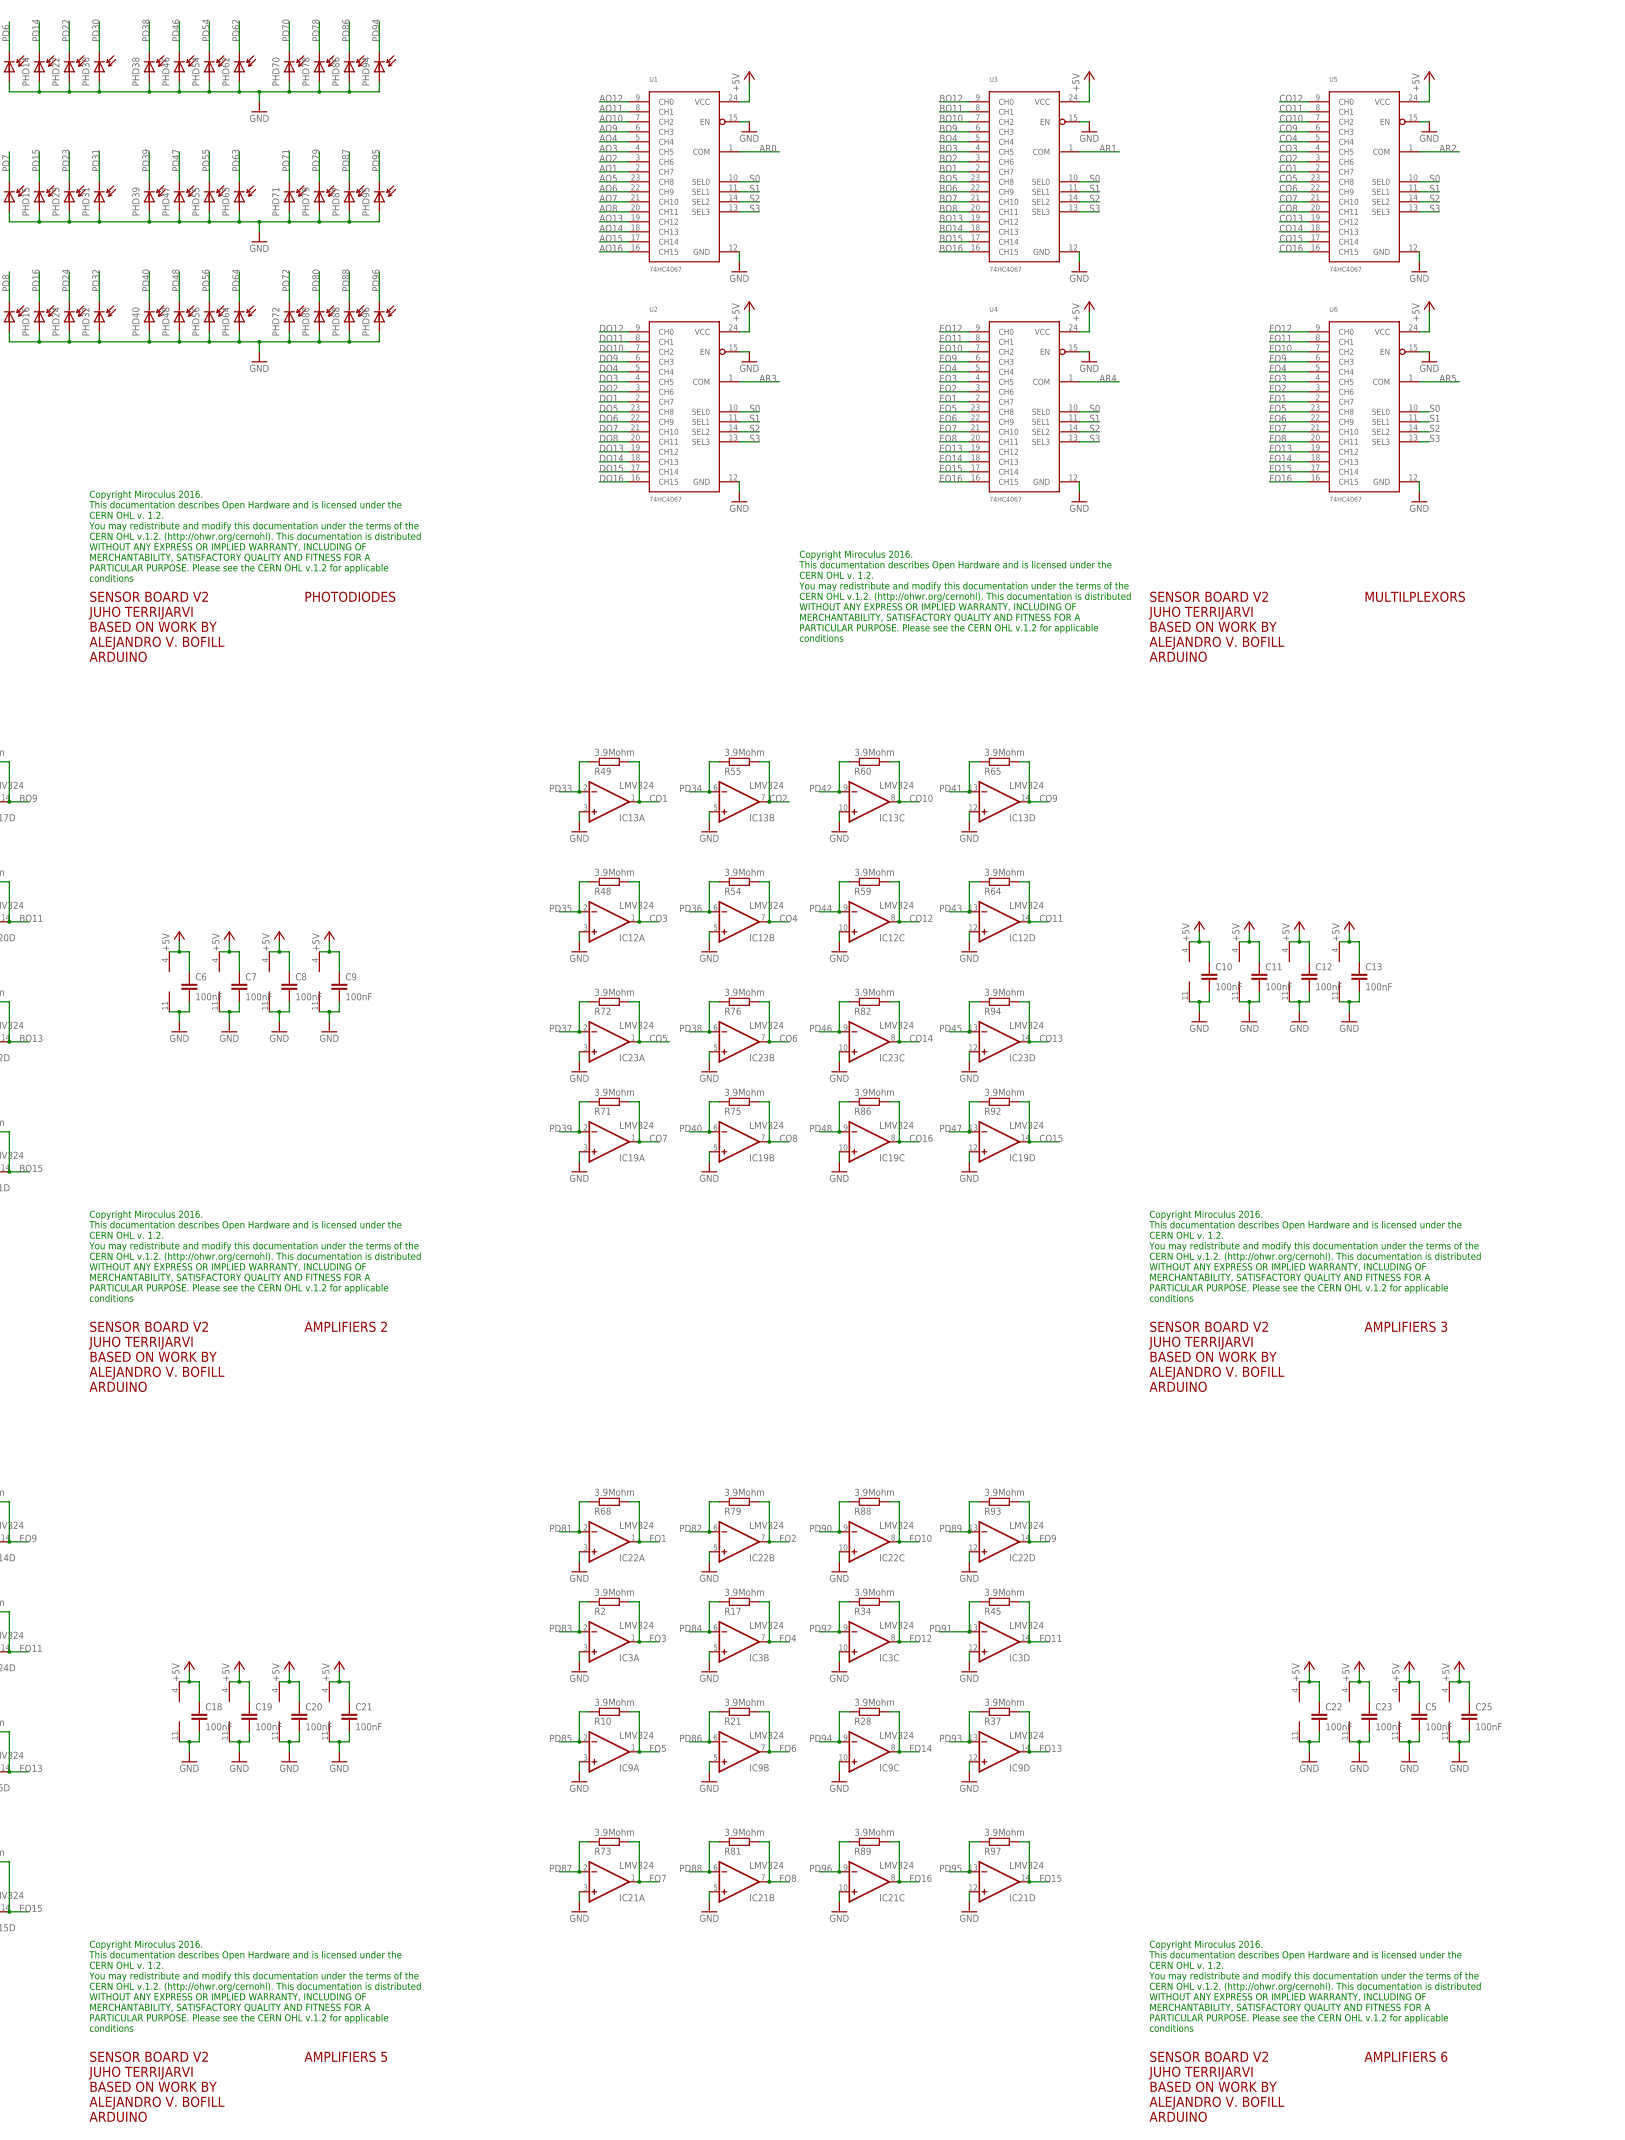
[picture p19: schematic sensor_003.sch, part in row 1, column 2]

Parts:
C1, C2, C3, C4, C5, C6, C7, C8, C9, C10, C11, C12, C13, C14, C15, C16, C17, C18, C19, C20, C21, C22, C23, C25: 100nF; C0603
FD1, FD2, FD3, FD4, FD5, FD6: FIDUCIALMOUNT; FIDUCIA-MOUNT
IC1, IC2, IC3, IC4, IC5, IC6, IC7, IC8, IC9, IC10, IC11, IC12, IC13, IC14, IC15, IC16, IC17, IC18, IC19, IC20, IC21, IC22, IC23, IC24: LMV324; SO14
J1, J2: 68710614522
PHD1, PHD2, PHD3, PHD4, PHD5, PHD6, PHD7, PHD8, PHD9, PHD10, PHD11, PHD12, PHD13, PHD14, PHD15, PHD16, PHD17, PHD18, PHD19, PHD20, PHD21, PHD22, PHD23, PHD24, PHD25, PHD26, PHD27, PHD28, PHD29, PHD30, PHD31, PHD32, PHD33, PHD34, PHD35, PHD36, PHD37, PHD38, PHD39, PHD40, PHD41, PHD42, PHD43, PHD44, PHD45, PHD46, PHD47, PHD48, PHD49, PHD50, PHD51, PHD52, PHD53, PHD54, PHD55, PHD56, PHD57, PHD58, PHD59, PHD60, PHD61, PHD62, PHD63, PHD64, PHD65, PHD66, PHD67, PHD68, PHD69, PHD70, PHD71, PHD72, PHD73, PHD74, PHD75, PHD76, PHD77, PHD78, PHD79, PHD80, PHD81, PHD82, PHD83, PHD84, PHD85, PHD86, PHD87, PHD88, PHD89, PHD90, PHD91, PHD92, PHD93, PHD94, PHD95, PHD96: CLS15-22C/L213G/TR8; PD_0.2
R1, R2, R3, R4, R5, R7, R8, R9, R10, R11, R12, R13, R14, R15, R16, R17, R18, R19, R20, R21, R22, R23, R24, R25, R26, R27, R28, R29, R30, R31, R32, R33, R34, R35, R36, R37, R38, R39, R40, R41, R42, R43, R44, R45, R46, R47, R48, R49, R50, R51, R52, R53, R54, R55, R56, R57, R58, R59, R60, R61, R62, R63, R64, R65, R66, R67, R68, R69, R70, R71, R72, R73, R74, R75, R76, R77, R78, R79, R80, R81, R82, R83, R84, R85, R86, R87, R88, R89, R90, R91, R92, R93, R94, R95, R96, R97: 3.9Mohm; R0603
U1, U2, U3, U4, U5, U6: 74HC4067; SSOP24

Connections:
+5V: C1.1, C2.1, C3.1, C4.1, C5.1, C6.1, C7.1, C8.1, C9.1, C10.1, C11.1, C12.1, C13.1, C14.1, C15.1, C16.1, C17.1, C18.1, C19.1, C20.1, C21.1, C22.1, C23.1, C25.1, IC1.4 (V+), IC2.4 (V+), IC3.4 (V+), IC4.4 (V+), IC5.4 (V+), IC6.4 (V+), IC7.4 (V+), IC8.4 (V+), IC9.4 (V+), IC10.4 (V+), IC11.4 (V+), IC12.4 (V+), IC13.4 (V+), IC14.4 (V+), IC15.4 (V+), IC16.4 (V+), IC17.4 (V+), IC18.4 (V+), IC19.4 (V+), IC20.4 (V+), IC21.4 (V+), IC22.4 (V+), IC23.4 (V+), IC24.4 (V+), J2.5, U1.24 (VCC), U2.24 (VCC), U3.24 (VCC), U4.24 (VCC), U5.24 (VCC), U6.24 (VCC)
AO1: IC10.1 (OUT), R11.2, U1.2 (CH7)
AO2: IC10.7 (OUT), R22.2, U1.3 (CH6)
AO3: IC11.1 (OUT), R12.2, U1.4 (CH5)
AO4: IC11.7 (OUT), R23.2, U1.5 (CH4)
AO5: IC8.1 (OUT), R9.2, U1.23 (CH8)
AO6: IC8.7 (OUT), R20.2, U1.22 (CH9)
AO7: IC7.1 (OUT), R8.2, U1.21 (CH10)
AO8: IC7.7 (OUT), R19.2, U1.20 (CH11)
AO9: IC10.14 (OUT), R38.2, U1.6 (CH3)
AO10: IC10.8 (OUT), R30.2, U1.7 (CH2)
AO11: IC11.14 (OUT), R39.2, U1.8 (CH1)
AO12: IC11.8 (OUT), R31.2, U1.9 (CH0)
AO13: IC8.14 (OUT), R36.2, U1.19 (CH12)
AO14: IC8.8 (OUT), R27.2, U1.18 (CH13)
AO15: IC7.14 (OUT), R35.2, U1.17 (CH14)
AO16: IC7.8 (OUT), R26.2, U1.16 (CH15)
AR0: J1.1, U1.1 (COM)
AR1: J1.2, U3.1 (COM)
AR2: J1.3, U5.1 (COM)
AR3: J1.4, U2.1 (COM)
AR4: J1.5, U4.1 (COM)
AR5: J1.6, U6.1 (COM)
BO1: IC17.1 (OUT), R66.2, U3.2 (CH7)
BO2: IC17.7 (OUT), R77.2, U3.3 (CH6)
BO3: IC20.1 (OUT), R70.2, U3.4 (CH5)
BO4: IC20.7 (OUT), R80.2, U3.5 (CH4)
BO5: IC2.1 (OUT), R5.2, U3.23 (CH8)
BO6: IC2.7 (OUT), R18.2, U3.22 (CH9)
BO7: IC1.1 (OUT), R4.2, U3.21 (CH10)
BO8: IC1.7 (OUT), R15.2, U3.20 (CH11)
BO9: IC17.14 (OUT), R90.2, U3.6 (CH3)
BO10: IC17.8 (OUT), R83.2, U3.7 (CH2)
BO11: IC20.14 (OUT), R96.2, U3.8 (CH1)
BO12: IC20.8 (OUT), R87.2, U3.9 (CH0)
BO13: IC2.14 (OUT), R41.2, U3.19 (CH12)
BO14: IC2.8 (OUT), R24.2, U3.18 (CH13)
BO15: IC1.14 (OUT), R44.2, U3.17 (CH14)
BO16: IC1.8 (OUT), R25.2, U3.16 (CH15)
CO1: IC13.1 (OUT), R49.2, U5.2 (CH7)
CO2: IC13.7 (OUT), R55.2, U5.3 (CH6)
CO3: IC12.1 (OUT), R48.2, U5.4 (CH5)
CO4: IC12.7 (OUT), R54.2, U5.5 (CH4)
CO5: IC23.1 (OUT), R72.2, U5.23 (CH8)
CO6: IC23.7 (OUT), R76.2, U5.22 (CH9)
CO7: IC19.1 (OUT), R71.2, U5.21 (CH10)
CO8: IC19.7 (OUT), R75.2, U5.20 (CH11)
CO9: IC13.14 (OUT), R65.2, U5.6 (CH3)
CO10: IC13.8 (OUT), R60.2, U5.7 (CH2)
CO11: IC12.14 (OUT), R64.2, U5.8 (CH1)
CO12: IC12.8 (OUT), R59.2, U5.9 (CH0)
CO13: IC23.14 (OUT), R94.2, U5.19 (CH12)
CO14: IC23.8 (OUT), R82.2, U5.18 (CH13)
CO15: IC19.14 (OUT), R92.2, U5.17 (CH14)
CO16: IC19.8 (OUT), R86.2, U5.16 (CH15)
DO1: IC6.1 (OUT), R1.2, U2.2 (CH7)
DO2: IC6.7 (OUT), R14.2, U2.3 (CH6)
DO3: IC16.1 (OUT), R47.2, U2.4 (CH5)
DO4: IC16.7 (OUT), R51.2, U2.5 (CH4)
DO5: IC18.1 (OUT), R69.2, U2.23 (CH8)
DO6: IC18.7 (OUT), R74.2, U2.22 (CH9)
DO7: IC4.1 (OUT), R3.2, U2.21 (CH10)
DO8: IC4.7 (OUT), R16.2, U2.20 (CH11)
DO9: IC6.14 (OUT), R42.2, U2.6 (CH3)
DO10: IC6.8 (OUT), R29.2, U2.7 (CH2)
DO11: IC16.14 (OUT), R61.2, U2.8 (CH1)
DO12: IC16.8 (OUT), R57.2, U2.9 (CH0)
DO13: IC18.14 (OUT), R91.2, U2.19 (CH12)
DO14: IC18.8 (OUT), R85.2, U2.18 (CH13)
DO15: IC4.14 (OUT), R40.2, U2.17 (CH14)
DO16: IC4.8 (OUT), R32.2, U2.16 (CH15)
EO1: IC14.1 (OUT), R46.2, U4.2 (CH7)
EO2: IC14.7 (OUT), R52.2, U4.3 (CH6)
EO3: IC24.1 (OUT), R67.2, U4.4 (CH5)
EO4: IC24.7 (OUT), R78.2, U4.5 (CH4)
EO5: IC5.1 (OUT), R7.2, U4.23 (CH8)
EO6: IC5.7 (OUT), R13.2, U4.22 (CH9)
EO7: IC15.1 (OUT), R50.2, U4.21 (CH10)
EO8: IC15.7 (OUT), R53.2, U4.20 (CH11)
EO9: IC14.14 (OUT), R62.2, U4.6 (CH3)
EO10: IC14.8 (OUT), R58.2, U4.7 (CH2)
EO11: IC24.14 (OUT), R95.2, U4.8 (CH1)
EO12: IC24.8 (OUT), R84.2, U4.9 (CH0)
EO13: IC5.14 (OUT), R43.2, U4.19 (CH12)
EO14: IC5.8 (OUT), R33.2, U4.18 (CH13)
EO15: IC15.14 (OUT), R63.2, U4.17 (CH14)
EO16: IC15.8 (OUT), R56.2, U4.16 (CH15)
FO1: IC22.1 (OUT), R68.2, U6.2 (CH7)
FO2: IC22.7 (OUT), R79.2, U6.3 (CH6)
FO3: IC3.1 (OUT), R2.2, U6.4 (CH5)
FO4: IC3.7 (OUT), R17.2, U6.5 (CH4)
FO5: IC9.1 (OUT), R10.2, U6.23 (CH8)
FO6: IC9.7 (OUT), R21.2, U6.22 (CH9)
FO7: IC21.1 (OUT), R73.2, U6.21 (CH10)
FO8: IC21.7 (OUT), R81.2, U6.20 (CH11)
FO9: IC22.14 (OUT), R93.2, U6.6 (CH3)
FO10: IC22.8 (OUT), R88.2, U6.7 (CH2)
FO11: IC3.14 (OUT), R45.2, U6.8 (CH1)
FO12: IC3.8 (OUT), R34.2, U6.9 (CH0)
FO13: IC9.14 (OUT), R37.2, U6.19 (CH12)
FO14: IC9.8 (OUT), R28.2, U6.18 (CH13)
FO15: IC21.14 (OUT), R97.2, U6.17 (CH14)
FO16: IC21.8 (OUT), R89.2, U6.16 (CH15)
GND: C1.2, C2.2, C3.2, C4.2, C5.2, C6.2, C7.2, C8.2, C9.2, C10.2, C11.2, C12.2, C13.2, C14.2, C15.2, C16.2, C17.2, C18.2, C19.2, C20.2, C21.2, C22.2, C23.2, C25.2, IC1.3 (+IN), IC1.5 (+IN), IC1.10 (+IN), IC1.11 (V-), IC1.12 (+IN), IC2.3 (+IN), IC2.5 (+IN), IC2.10 (+IN), IC2.11 (V-), IC2.12 (+IN), IC3.3 (+IN), IC3.5 (+IN), IC3.10 (+IN), IC3.11 (V-), IC3.12 (+IN), IC4.3 (+IN), IC4.5 (+IN), IC4.10 (+IN), IC4.11 (V-), IC4.12 (+IN), IC5.3 (+IN), IC5.5 (+IN), IC5.10 (+IN), IC5.11 (V-), IC5.12 (+IN), IC6.3 (+IN), IC6.5 (+IN), IC6.10 (+IN), IC6.11 (V-), IC6.12 (+IN), IC7.3 (+IN), IC7.5 (+IN), IC7.10 (+IN), IC7.11 (V-), IC7.12 (+IN), IC8.3 (+IN), IC8.5 (+IN), IC8.10 (+IN), IC8.11 (V-), IC8.12 (+IN), IC9.3 (+IN), IC9.5 (+IN), IC9.10 (+IN), IC9.11 (V-), IC9.12 (+IN), IC10.3 (+IN), IC10.5 (+IN), IC10.10 (+IN), IC10.11 (V-), IC10.12 (+IN), IC11.3 (+IN), IC11.5 (+IN), IC11.10 (+IN), IC11.11 (V-), IC11.12 (+IN), IC12.3 (+IN), IC12.5 (+IN), IC12.10 (+IN), IC12.11 (V-), IC12.12 (+IN), IC13.3 (+IN), IC13.5 (+IN), IC13.10 (+IN), IC13.11 (V-), IC13.12 (+IN), IC14.3 (+IN), IC14.5 (+IN), IC14.10 (+IN), IC14.11 (V-), IC14.12 (+IN), IC15.3 (+IN), IC15.5 (+IN), IC15.10 (+IN), IC15.11 (V-), IC15.12 (+IN), IC16.3 (+IN), IC16.5 (+IN), IC16.10 (+IN), IC16.11 (V-), IC16.12 (+IN), IC17.3 (+IN), IC17.5 (+IN), IC17.10 (+IN), IC17.11 (V-), IC17.12 (+IN), IC18.3 (+IN), IC18.5 (+IN), IC18.10 (+IN), IC18.11 (V-), IC18.12 (+IN), IC19.3 (+IN), IC19.5 (+IN), IC19.10 (+IN), IC19.11 (V-), IC19.12 (+IN), IC20.3 (+IN), IC20.5 (+IN), IC20.10 (+IN), IC20.11 (V-), IC20.12 (+IN), IC21.3 (+IN), IC21.5 (+IN), IC21.10 (+IN), IC21.11 (V-), IC21.12 (+IN), IC22.3 (+IN), IC22.5 (+IN), IC22.10 (+IN), IC22.11 (V-), IC22.12 (+IN), IC23.3 (+IN), IC23.5 (+IN), IC23.10 (+IN), IC23.11 (V-), IC23.12 (+IN), IC24.3 (+IN), IC24.5 (+IN), IC24.10 (+IN), IC24.11 (V-), IC24.12 (+IN), J2.6, PHD1.1, PHD1.2 (1), PHD2.1, PHD2.2 (1), PHD3.1, PHD3.2 (1), PHD4.1, PHD4.2 (1), PHD5.1, PHD5.2 (1), PHD6.1, PHD6.2 (1), PHD7.1, PHD7.2 (1), PHD8.1, PHD8.2 (1), PHD9.1, PHD9.2 (1), PHD10.1, PHD10.2 (1), PHD11.1, PHD11.2 (1), PHD12.1, PHD12.2 (1), PHD13.1, PHD13.2 (1), PHD14.1, PHD14.2 (1), PHD15.1, PHD15.2 (1), PHD16.1, PHD16.2 (1), PHD17.1, PHD17.2 (1), PHD18.1, PHD18.2 (1), PHD19.1, PHD19.2 (1), PHD20.1, PHD20.2 (1), PHD21.1, PHD21.2 (1), PHD22.1, PHD22.2 (1), PHD23.1, PHD23.2 (1), PHD24.1, PHD24.2 (1), PHD25.1, PHD25.2 (1), PHD26.1, PHD26.2 (1), PHD27.1, PHD27.2 (1), PHD28.1, PHD28.2 (1), PHD29.1, PHD29.2 (1), PHD30.1, PHD30.2 (1), PHD31.1, PHD31.2 (1), PHD32.1, PHD32.2 (1), PHD33.1, PHD33.2 (1), PHD34.1, PHD34.2 (1), PHD35.1, PHD35.2 (1), PHD36.1, PHD36.2 (1), PHD37.1, PHD37.2 (1), PHD38.1, PHD38.2 (1), PHD39.1, PHD39.2 (1), PHD40.1, PHD40.2 (1), PHD41.1, PHD41.2 (1), PHD42.1, PHD42.2 (1), PHD43.1, PHD43.2 (1), PHD44.1, PHD44.2 (1), PHD45.1, PHD45.2 (1), PHD46.1, PHD46.2 (1), PHD47.1, PHD47.2 (1), PHD48.1, PHD48.2 (1), PHD49.1, PHD49.2 (1), PHD50.1, PHD50.2 (1), PHD51.1, PHD51.2 (1), PHD52.1, PHD52.2 (1), PHD53.1, PHD53.2 (1), PHD54.1, PHD54.2 (1), PHD55.1, PHD55.2 (1), PHD56.1, PHD56.2 (1), PHD57.1, PHD57.2 (1), PHD58.1, PHD58.2 (1), PHD59.1, PHD59.2 (1), PHD60.1, PHD60.2 (1), PHD61.1, PHD61.2 (1), PHD62.1, PHD62.2 (1), PHD63.1, PHD63.2 (1), PHD64.1, PHD64.2 (1), PHD65.1, PHD65.2 (1), PHD66.1, PHD66.2 (1), PHD67.1, PHD67.2 (1), PHD68.1, PHD68.2 (1), PHD69.1, PHD69.2 (1), PHD70.1, PHD70.2 (1), PHD71.1, PHD71.2 (1), PHD72.1, PHD72.2 (1), PHD73.1, PHD73.2 (1), PHD74.1, PHD74.2 (1), PHD75.1, PHD75.2 (1), PHD76.1, PHD76.2 (1), PHD77.1, PHD77.2 (1), PHD78.1, PHD78.2 (1), PHD79.1, PHD79.2 (1), PHD80.1, PHD80.2 (1), PHD81.1, PHD81.2 (1), PHD82.1, PHD82.2 (1), PHD83.1, PHD83.2 (1), PHD84.1, PHD84.2 (1), PHD85.1, PHD85.2 (1), PHD86.1, PHD86.2 (1), PHD87.1, PHD87.2 (1), PHD88.1, PHD88.2 (1), PHD89.1, PHD89.2 (1), PHD90.1, PHD90.2 (1), PHD91.1, PHD91.2 (1), PHD92.1, PHD92.2 (1), PHD93.1, PHD93.2 (1), PHD94.1, PHD94.2 (1), PHD95.1, PHD95.2 (1), PHD96.1, PHD96.2 (1), U1.12 (GND), U1.15 (EN), U2.12 (GND), U2.15 (EN), U3.12 (GND), U3.15 (EN), U4.12 (GND), U4.15 (EN), U5.12 (GND), U5.15 (EN), U6.12 (GND), U6.15 (EN)
PD1: IC10.2 (-IN), PHD1.3 (2), PHD1.4 (2), R11.1
PD2: IC10.6 (-IN), PHD2.3 (2), PHD2.4 (2), R22.1
PD3: IC11.2 (-IN), PHD3.3 (2), PHD3.4 (2), R12.1
PD4: IC11.6 (-IN), PHD4.3 (2), PHD4.4 (2), R23.1
PD5: IC8.2 (-IN), PHD5.3 (2), PHD5.4 (2), R9.1
PD6: IC8.6 (-IN), PHD6.3 (2), PHD6.4 (2), R20.1
PD7: IC7.2 (-IN), PHD7.3 (2), PHD7.4 (2), R8.1
PD8: IC7.6 (-IN), PHD8.3 (2), PHD8.4 (2), R19.1
PD9: IC10.13 (-IN), PHD9.3 (2), PHD9.4 (2), R38.1
PD10: IC10.9 (-IN), PHD10.3 (2), PHD10.4 (2), R30.1
PD11: IC11.13 (-IN), PHD11.3 (2), PHD11.4 (2), R39.1
PD12: IC11.9 (-IN), PHD12.3 (2), PHD12.4 (2), R31.1
PD13: IC8.13 (-IN), PHD13.3 (2), PHD13.4 (2), R36.1
PD14: IC8.9 (-IN), PHD14.3 (2), PHD14.4 (2), R27.1
PD15: IC7.13 (-IN), PHD15.3 (2), PHD15.4 (2), R35.1
PD16: IC7.9 (-IN), PHD16.3 (2), PHD16.4 (2), R26.1
PD17: IC17.2 (-IN), PHD17.3 (2), PHD17.4 (2), R66.1
PD18: IC17.6 (-IN), PHD18.3 (2), PHD18.4 (2), R77.1
PD19: IC20.2 (-IN), PHD19.3 (2), PHD19.4 (2), R70.1
PD20: IC20.6 (-IN), PHD20.3 (2), PHD20.4 (2), R80.1
PD21: IC2.2 (-IN), PHD21.3 (2), PHD21.4 (2), R5.1
PD22: IC2.6 (-IN), PHD22.3 (2), PHD22.4 (2), R18.1
PD23: IC1.2 (-IN), PHD23.3 (2), PHD23.4 (2), R4.1
PD24: IC1.6 (-IN), PHD24.3 (2), PHD24.4 (2), R15.1
PD25: IC17.13 (-IN), PHD25.3 (2), PHD25.4 (2), R90.1
PD26: IC17.9 (-IN), PHD26.3 (2), PHD26.4 (2), R83.1
PD27: IC20.13 (-IN), PHD27.3 (2), PHD27.4 (2), R96.1
PD28: IC20.9 (-IN), PHD28.3 (2), PHD28.4 (2), R87.1
PD29: IC2.13 (-IN), PHD29.3 (2), PHD29.4 (2), R41.1
PD30: IC2.9 (-IN), PHD30.3 (2), PHD30.4 (2), R24.1
PD31: IC1.13 (-IN), PHD31.3 (2), PHD31.4 (2), R44.1
PD32: IC1.9 (-IN), PHD32.3 (2), PHD32.4 (2), R25.1
PD33: IC13.2 (-IN), PHD33.3 (2), PHD33.4 (2), R49.1
PD34: IC13.6 (-IN), PHD34.3 (2), PHD34.4 (2), R55.1
PD35: IC12.2 (-IN), PHD35.3 (2), PHD35.4 (2), R48.1
PD36: IC12.6 (-IN), PHD36.3 (2), PHD36.4 (2), R54.1
PD37: IC23.2 (-IN), PHD37.3 (2), PHD37.4 (2), R72.1
PD38: IC23.6 (-IN), PHD38.3 (2), PHD38.4 (2), R76.1
PD39: IC19.2 (-IN), PHD39.3 (2), PHD39.4 (2), R71.1
PD40: IC19.6 (-IN), PHD40.3 (2), PHD40.4 (2), R75.1
PD41: IC13.13 (-IN), PHD41.3 (2), PHD41.4 (2), R65.1
PD42: IC13.9 (-IN), PHD42.3 (2), PHD42.4 (2), R60.1
PD43: IC12.13 (-IN), PHD43.3 (2), PHD43.4 (2), R64.1
PD44: IC12.9 (-IN), PHD44.3 (2), PHD44.4 (2), R59.1
PD45: IC23.13 (-IN), PHD45.3 (2), PHD45.4 (2), R94.1
PD46: IC23.9 (-IN), PHD46.3 (2), PHD46.4 (2), R82.1
PD47: IC19.13 (-IN), PHD47.3 (2), PHD47.4 (2), R92.1
PD48: IC19.9 (-IN), PHD48.3 (2), PHD48.4 (2), R86.1
PD49: IC6.2 (-IN), PHD49.3 (2), PHD49.4 (2), R1.1
PD50: IC6.6 (-IN), PHD50.3 (2), PHD50.4 (2), R14.1
PD51: IC16.2 (-IN), PHD51.3 (2), PHD51.4 (2), R47.1
PD52: IC16.6 (-IN), PHD52.3 (2), PHD52.4 (2), R51.1
PD53: IC18.2 (-IN), PHD53.3 (2), PHD53.4 (2), R69.1
PD54: IC18.6 (-IN), PHD54.3 (2), PHD54.4 (2), R74.1
PD55: IC4.2 (-IN), PHD55.3 (2), PHD55.4 (2), R3.1
PD56: IC4.6 (-IN), PHD56.3 (2), PHD56.4 (2), R16.1
PD57: IC6.13 (-IN), PHD57.3 (2), PHD57.4 (2), R42.1
PD58: IC6.9 (-IN), PHD58.3 (2), PHD58.4 (2), R29.1
PD59: IC16.13 (-IN), PHD59.3 (2), PHD59.4 (2), R61.1
PD60: IC16.9 (-IN), PHD60.3 (2), PHD60.4 (2), R57.1
PD61: IC18.13 (-IN), PHD61.3 (2), PHD61.4 (2), R91.1
PD62: IC18.9 (-IN), PHD62.3 (2), PHD62.4 (2), R85.1
PD63: IC4.13 (-IN), PHD63.3 (2), PHD63.4 (2), R40.1
PD64: IC4.9 (-IN), PHD64.3 (2), PHD64.4 (2), R32.1
PD65: IC14.2 (-IN), PHD65.3 (2), PHD65.4 (2), R46.1
PD66: IC14.6 (-IN), PHD66.3 (2), PHD66.4 (2), R52.1
PD67: IC24.2 (-IN), PHD67.3 (2), PHD67.4 (2), R67.1
PD68: IC24.6 (-IN), PHD68.3 (2), PHD68.4 (2), R78.1
PD69: IC5.2 (-IN), PHD69.3 (2), PHD69.4 (2), R7.1
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

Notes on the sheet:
SENSOR BOARD V2 JUHO TERRIJARVI BASED ON WORK BY ALEJANDRO V. BOFILL ARDUINO
POWER
POWER/PORTS
PHOTODIODES
AMPLIFIERS 1
AMPLIFIERS 2
AMPLIFIERS 3
AMPLIFIERS 4
AMPLIFIERS 5
AMPLIFIERS 6
MULTILPLEXORS
Copyright Miroculus 2016. This documentation describes Open Hardware and is licensed under the CERN OHL v. 1.2. You may redistribute and modify this documentation under the terms of the CERN OHL v.1.2. (http://ohwr.org/cernohl). This documentation is distributed WITHOUT ANY EXPRESS OR IMPLIED WARRA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

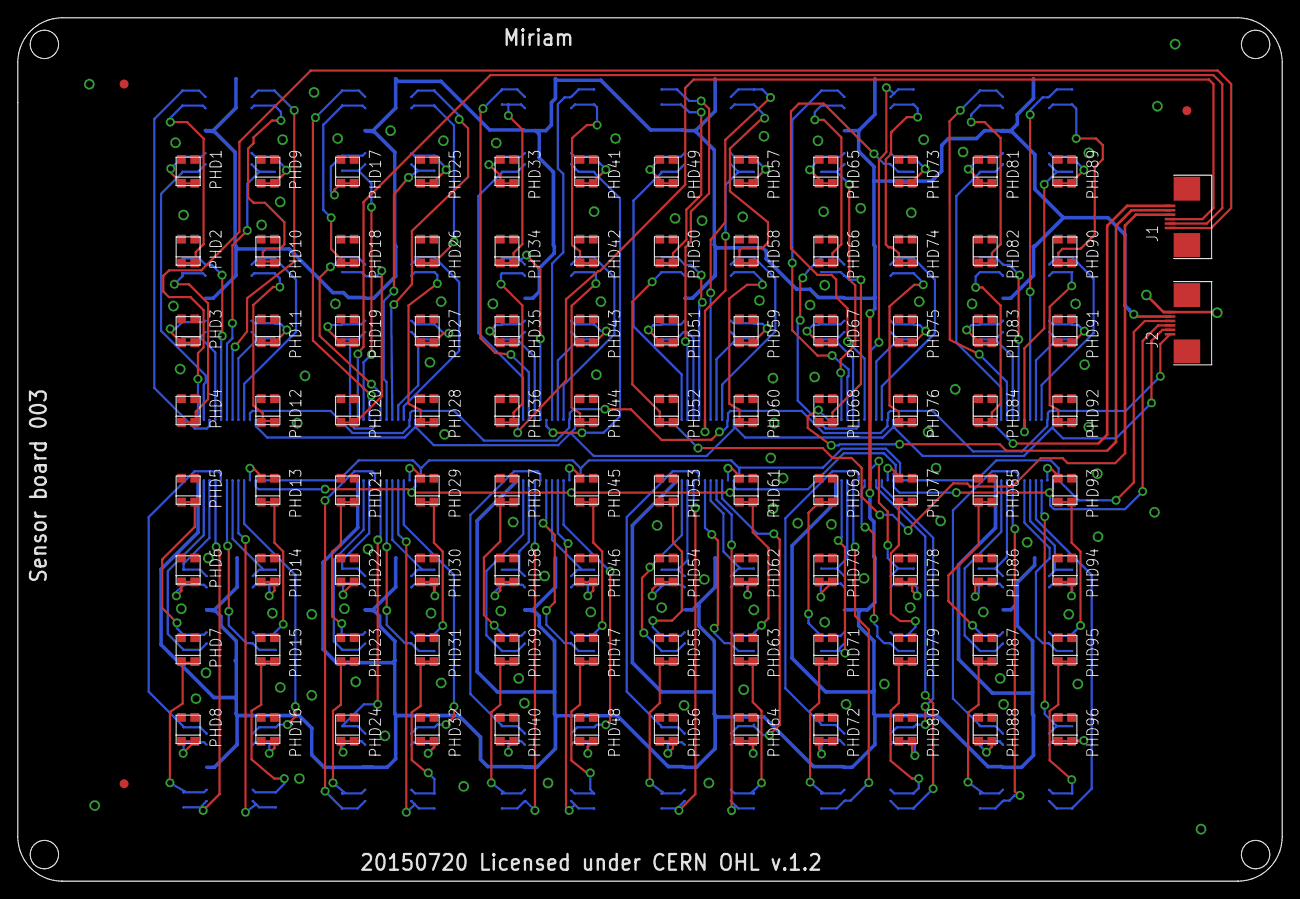
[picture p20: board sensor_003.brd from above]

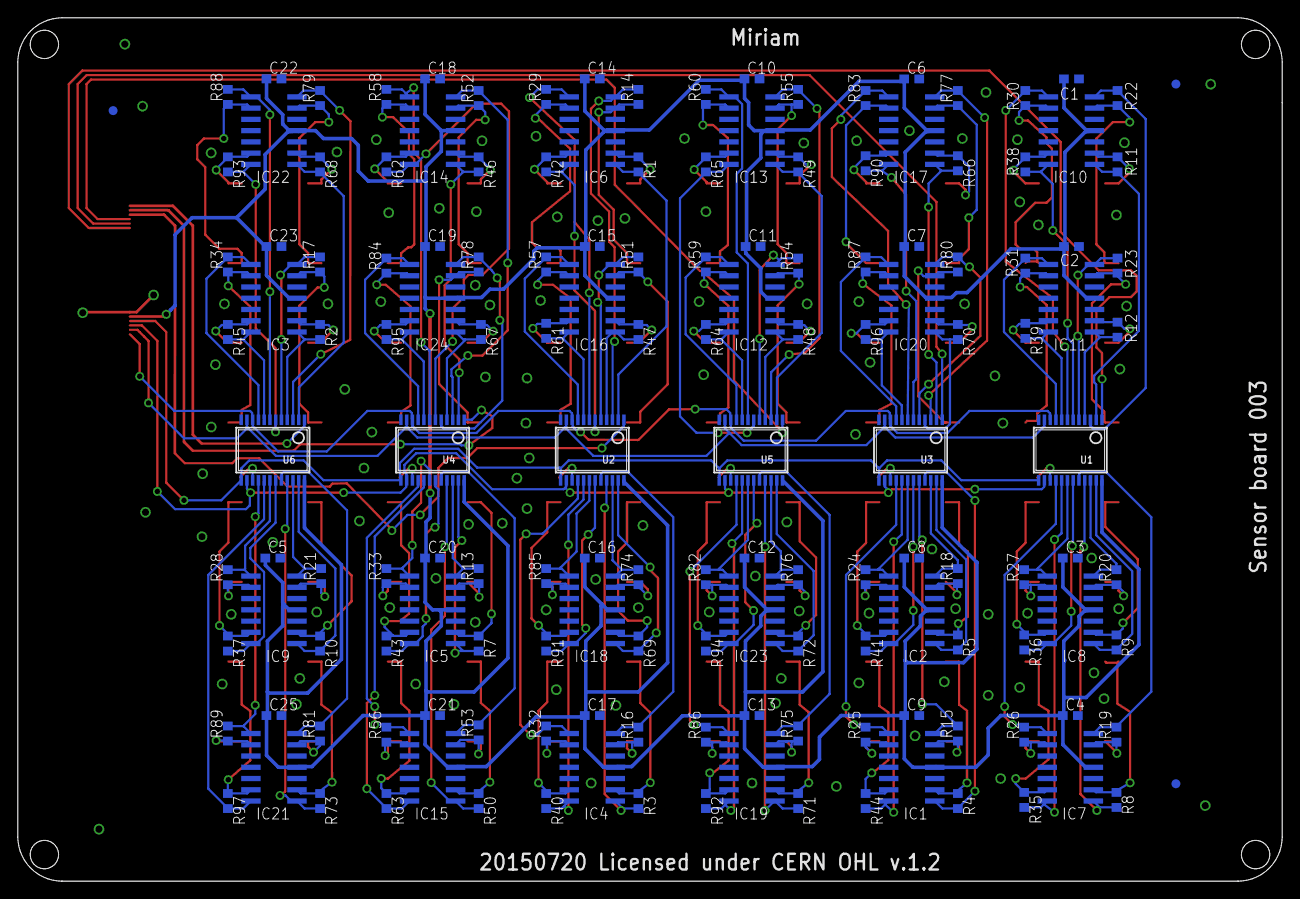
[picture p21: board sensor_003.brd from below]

Board: 2 copper layers, 142.8 x 97.5 mm, 254 parts (153 on the bottom side), 204 nets.

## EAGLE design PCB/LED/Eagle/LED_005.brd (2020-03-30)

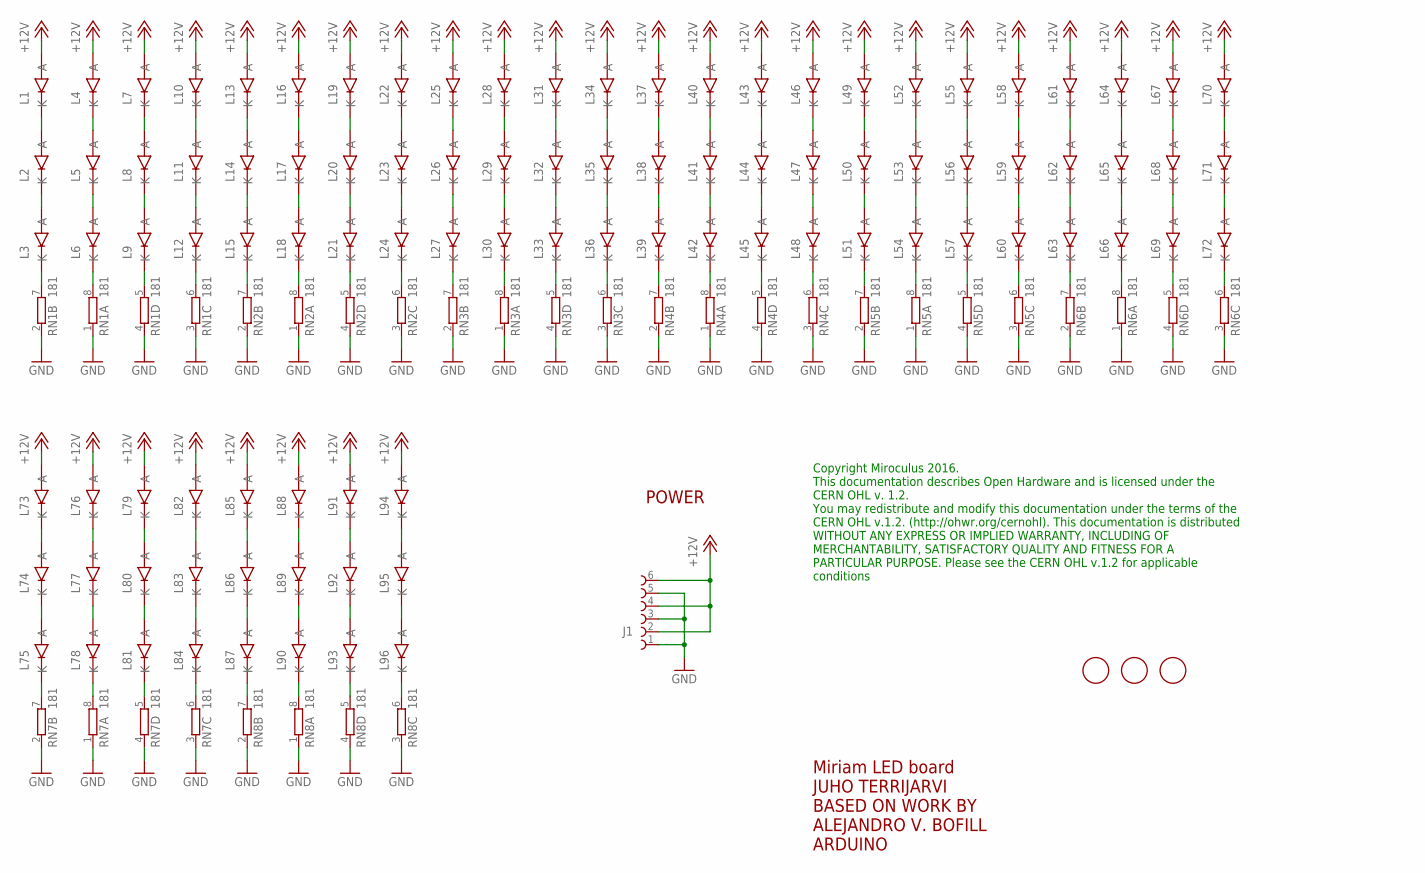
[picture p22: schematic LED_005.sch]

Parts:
FD1, FD2, FD3: FIDUCIALMOUNT; FIDUCIA-MOUNT
J1: 68710614522
L1, L2, L3, L4, L5, L6, L7, L8, L9, L10, L11, L12, L13, L14, L15, L16, L17, L18, L19, L20, L21, L22, L23, L24, L25, L26, L27, L28, L29, L30, L31, L32, L33, L34, L35, L36, L37, L38, L39, L40, L41, L42, L43, L44, L45, L46, L47, L48, L49, L50, L51, L52, L53, L54, L55, L56, L57, L58, L59, L60, L61, L62, L63, L64, L65, L66, L67, L68, L69, L70, L71, L72, L73, L74, L75, L76, L77, L78, L79, L80, L81, L82, L83, L84, L85, L86, L87, L88, L89, L90, L91, L92, L93, L94, L95, L96: KA-2810AQBS-G; LED_0.2
RN1, RN2, RN3, RN4, RN5, RN6, RN7, RN8: 181; CAY16

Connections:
+12V: J1.2, J1.4, J1.6, L1.2 (A), L4.2 (A), L7.2 (A), L10.2 (A), L13.2 (A), L16.2 (A), L19.2 (A), L22.2 (A), L25.2 (A), L28.2 (A), L31.2 (A), L34.2 (A), L37.2 (A), L40.2 (A), L43.2 (A), L46.2 (A), L49.2 (A), L52.2 (A), L55.2 (A), L58.2 (A), L61.2 (A), L64.2 (A), L67.2 (A), L70.2 (A), L73.2 (A), L76.2 (A), L79.2 (A), L82.2 (A), L85.2 (A), L88.2 (A), L91.2 (A), L94.2 (A)
GND: J1.1, J1.3, J1.5, RN1.1, RN1.2 (1), RN1.3 (1), RN1.4 (1), RN2.1, RN2.2 (1), RN2.3 (1), RN2.4 (1), RN3.1, RN3.2 (1), RN3.3 (1), RN3.4 (1), RN4.1, RN4.2 (1), RN4.3 (1), RN4.4 (1), RN5.1, RN5.2 (1), RN5.3 (1), RN5.4 (1), RN6.1, RN6.2 (1), RN6.3 (1), RN6.4 (1), RN7.1, RN7.2 (1), RN7.3 (1), RN7.4 (1), RN8.1, RN8.2 (1), RN8.3 (1), RN8.4 (1)
unnamed: L1.1 (K), L2.2 (A)
unnamed: L2.1 (K), L3.2 (A)
unnamed: L3.1 (K), RN1.7 (2)
unnamed: L4.1 (K), L5.2 (A)
unnamed: L5.1 (K), L6.2 (A)
unnamed: L6.1 (K), RN1.8 (2)
unnamed: L7.1 (K), L8.2 (A)
unnamed: L8.1 (K), L9.2 (A)
unnamed: L9.1 (K), RN1.5 (2)
unnamed: L10.1 (K), L11.2 (A)
unnamed: L11.1 (K), L12.2 (A)
unnamed: L12.1 (K), RN1.6 (2)
unnamed: L13.1 (K), L14.2 (A)
unnamed: L14.1 (K), L15.2 (A)
unnamed: L16.1 (K), L17.2 (A)
unnamed: L17.1 (K), L18.2 (A)
unnamed: L19.1 (K), L20.2 (A)
unnamed: L20.1 (K), L21.2 (A)
unnamed: L22.1 (K), L23.2 (A)
unnamed: L23.1 (K), L24.2 (A)
unnamed: L15.1 (K), RN2.7 (2)
unnamed: L18.1 (K), RN2.8 (2)
unnamed: L21.1 (K), RN2.5 (2)
unnamed: L24.1 (K), RN2.6 (2)
unnamed: L25.1 (K), L26.2 (A)
unnamed: L26.1 (K), L27.2 (A)
unnamed: L28.1 (K), L29.2 (A)
unnamed: L29.1 (K), L30.2 (A)
unnamed: L31.1 (K), L32.2 (A)
unnamed: L32.1 (K), L33.2 (A)
unnamed: L34.1 (K), L35.2 (A)
unnamed: L35.1 (K), L36.2 (A)
unnamed: L27.1 (K), RN3.7 (2)
unnamed: L30.1 (K), RN3.8 (2)
unnamed: L33.1 (K), RN3.5 (2)
unnamed: L36.1 (K), RN3.6 (2)
unnamed: L37.1 (K), L38.2 (A)
unnamed: L38.1 (K), L39.2 (A)
unnamed: L40.1 (K), L41.2 (A)
unnamed: L41.1 (K), L42.2 (A)
unnamed: L43.1 (K), L44.2 (A)
unnamed: L44.1 (K), L45.2 (A)
unnamed: L46.1 (K), L47.2 (A)
unnamed: L47.1 (K), L48.2 (A)
unnamed: L39.1 (K), RN4.7 (2)
unnamed: L42.1 (K), RN4.8 (2)
unnamed: L45.1 (K), RN4.5 (2)
unnamed: L48.1 (K), RN4.6 (2)
unnamed: L49.1 (K), L50.2 (A)
unnamed: L50.1 (K), L51.2 (A)
unnamed: L52.1 (K), L53.2 (A)
unnamed: L53.1 (K), L54.2 (A)
unnamed: L55.1 (K), L56.2 (A)
unnamed: L56.1 (K), L57.2 (A)
unnamed: L58.1 (K), L59.2 (A)
unnamed: L59.1 (K), L60.2 (A)
unnamed: L51.1 (K), RN5.7 (2)
unnamed: L54.1 (K), RN5.8 (2)
unnamed: L57.1 (K), RN5.5 (2)
unnamed: L60.1 (K), RN5.6 (2)
unnamed: L61.1 (K), L62.2 (A)
unnamed: L62.1 (K), L63.2 (A)
unnamed: L64.1 (K), L65.2 (A)
unnamed: L65.1 (K), L66.2 (A)
unnamed: L67.1 (K), L68.2 (A)
unnamed: L68.1 (K), L69.2 (A)
unnamed: L70.1 (K), L71.2 (A)
unnamed: L71.1 (K), L72.2 (A)
unnamed: L63.1 (K), RN6.7 (2)
unnamed: L66.1 (K), RN6.8 (2)
unnamed: L69.1 (K), RN6.5 (2)
unnamed: L72.1 (K), RN6.6 (2)
unnamed: L73.1 (K), L74.2 (A)
unnamed: L74.1 (K), L75.2 (A)
unnamed: L76.1 (K), L77.2 (A)
unnamed: L77.1 (K), L78.2 (A)
unnamed: L79.1 (K), L80.2 (A)
unnamed: L80.1 (K), L81.2 (A)
unnamed: L82.1 (K), L83.2 (A)
unnamed: L83.1 (K), L84.2 (A)
unnamed: L96.1 (K), RN8.6 (2)
unnamed: L93.1 (K), RN8.5 (2)
unnamed: L90.1 (K), RN8.8 (2)
unnamed: L87.1 (K), RN8.7 (2)
unnamed: L85.1 (K), L86.2 (A)
unnamed: L86.1 (K), L87.2 (A)
unnamed: L88.1 (K), L89.2 (A)
unnamed: L89.1 (K), L90.2 (A)
unnamed: L91.1 (K), L92.2 (A)
unnamed: L92.1 (K), L93.2 (A)
unnamed: L94.1 (K), L95.2 (A)
unnamed: L95.1 (K), L96.2 (A)
unnamed: L84.1 (K), RN7.6 (2)
unnamed: L81.1 (K), RN7.5 (2)
unnamed: L78.1 (K), RN7.8 (2)
unnamed: L75.1 (K), RN7.7 (2)

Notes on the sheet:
POWER
Miriam LED board JUHO TERRIJARVI BASED ON WORK BY ALEJANDRO V. BOFILL ARDUINO
Copyright Miroculus 2016. This documentation describes Open Hardware and is licensed under the CERN OHL v. 1.2. You may redistribute and modify this documentation under the terms of the CERN OHL v.1.2. (http://ohwr.org/cernohl). This documentation is distributed WITHOUT ANY EXPRESS OR IMPLIED WARRA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

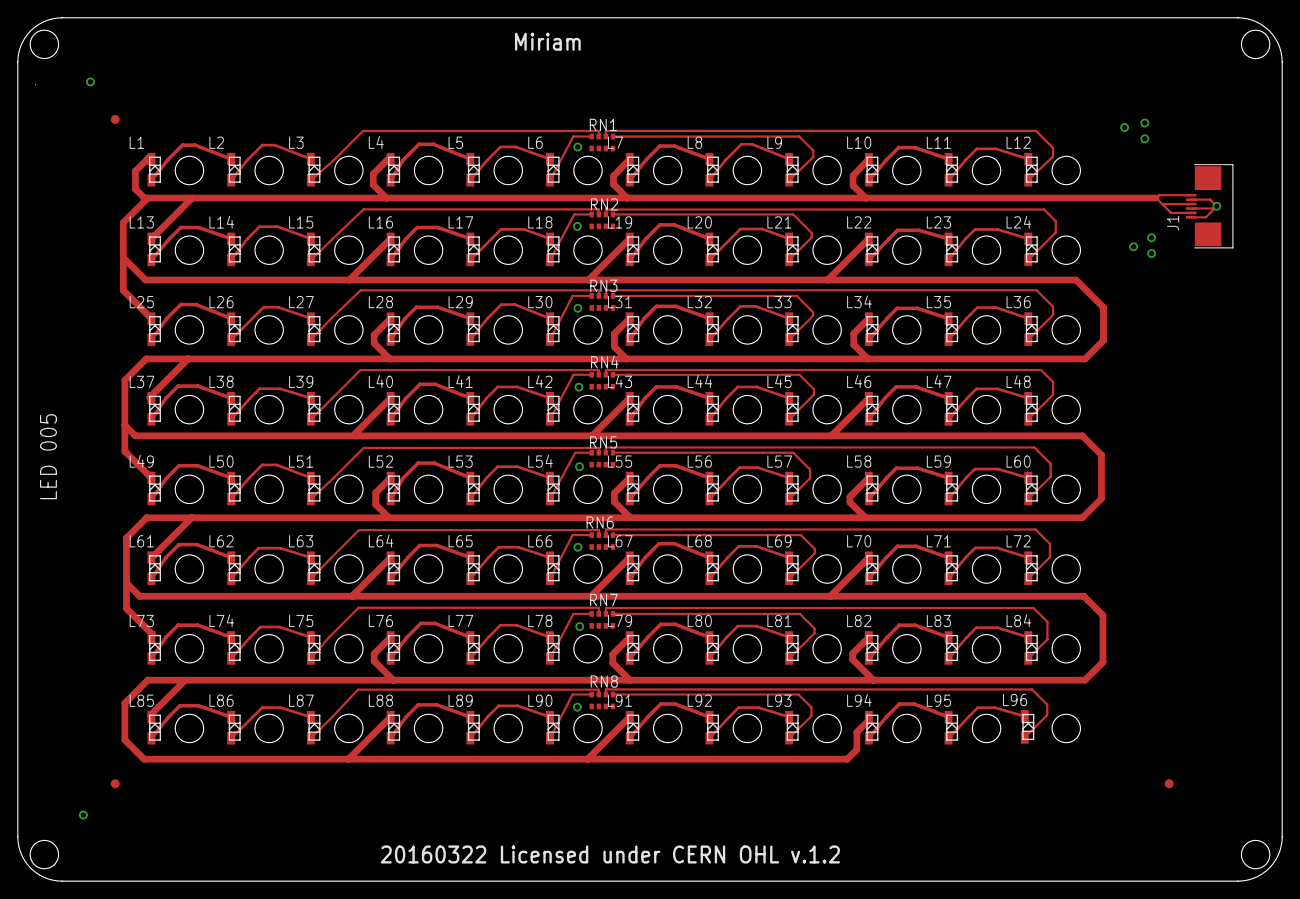
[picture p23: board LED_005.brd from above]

Board: 2 copper layers, 142.8 x 97.5 mm, 108 parts (0 on the bottom side), 98 nets.

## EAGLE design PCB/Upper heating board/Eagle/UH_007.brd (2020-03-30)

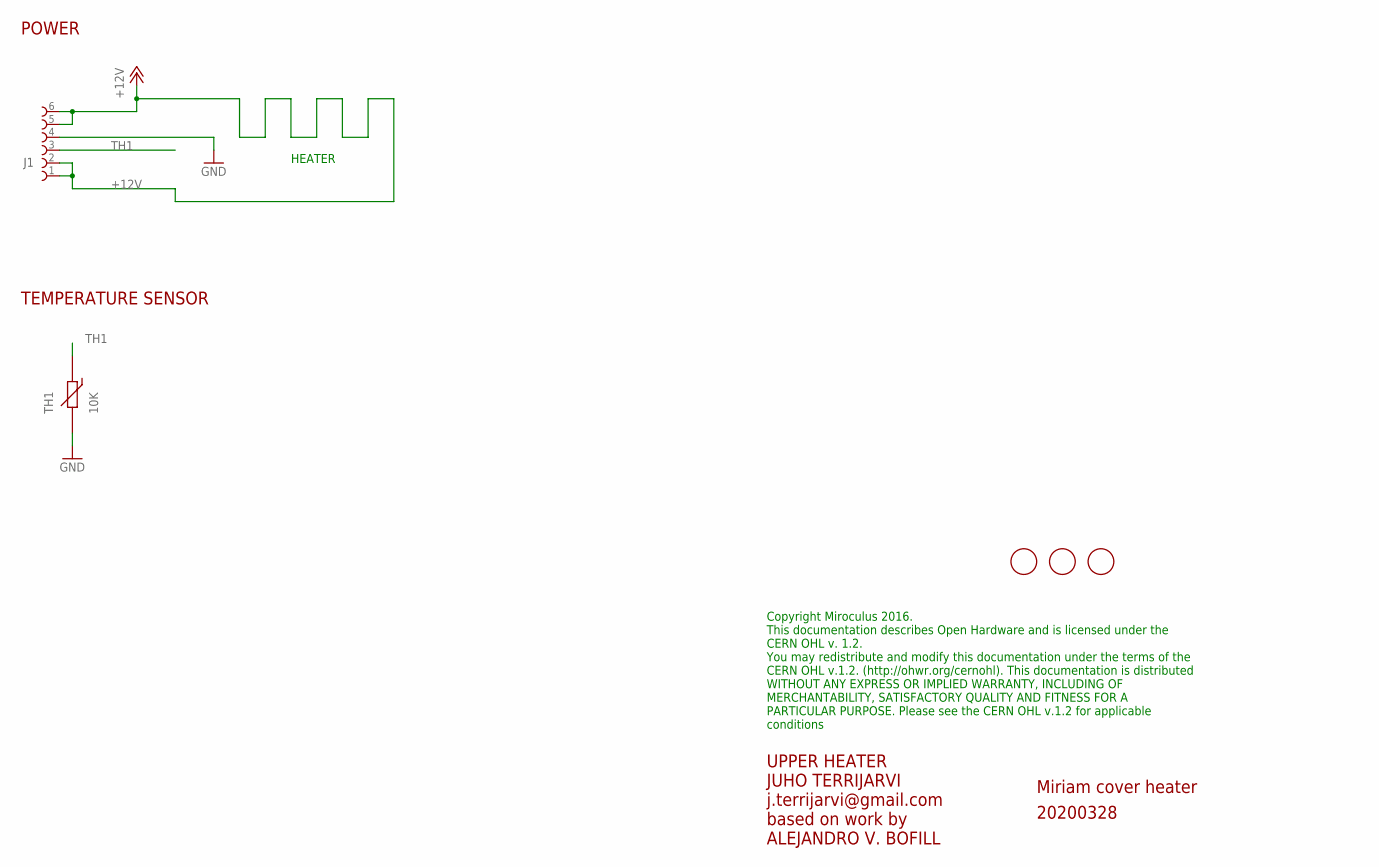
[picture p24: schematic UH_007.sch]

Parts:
FD1, FD2, FD3: FIDUCIALMOUNT; FIDUCIA-MOUNT
J1: 68710614522
TH1: 10K; THERMISTOR_SMD_0603

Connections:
+12V: J1.1, J1.2, J1.5, J1.6
GND: J1.4, TH1.2
TH1: J1.3, TH1.1

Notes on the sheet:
POWER
UPPER HEATER JUHO TERRIJARVI j.terrijarvi@gmail.com based on work by ALEJANDRO V. BOFILL
HEATER
TEMPERATURE SENSOR
Miriam cover heater
20200328
Copyright Miroculus 2016. This documentation describes Open Hardware and is licensed under the CERN OHL v. 1.2. You may redistribute and modify this documentation under the terms of the CERN OHL v.1.2. (http://ohwr.org/cernohl). This documentation is distributed WITHOUT ANY EXPRESS OR IMPLIED WARRA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

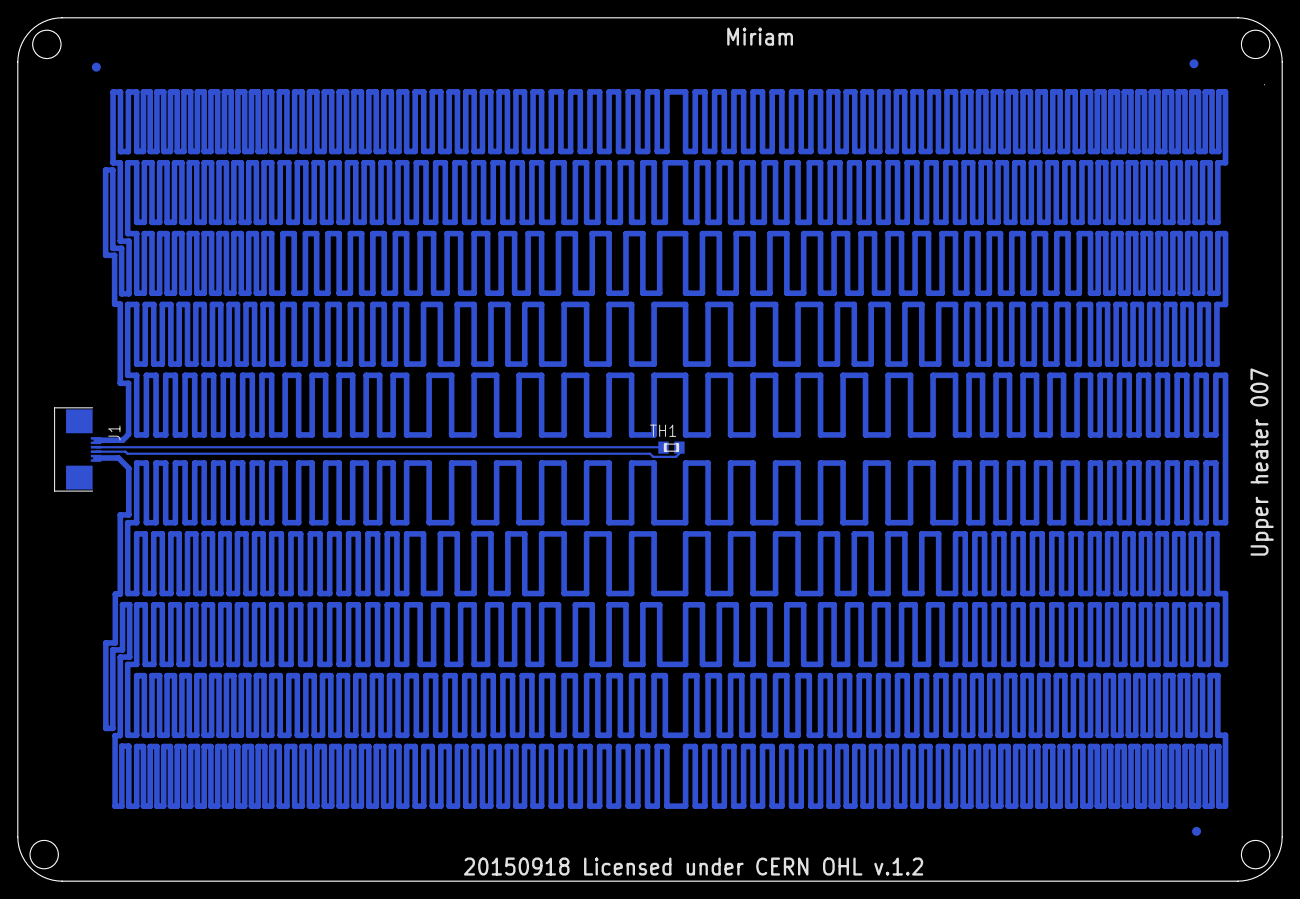
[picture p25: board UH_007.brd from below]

Board: 2 copper layers, 142.8 x 97.5 mm, 5 parts (5 on the bottom side), 3 nets.

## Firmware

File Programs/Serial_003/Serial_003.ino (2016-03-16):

/*
 * Miriam control
 *  
 * Miriam is an isothermal amplification unit capable of real time detection that supports a 96 well PCR plate
 * This firmware allows the control over serial port string messages
 *
 * The basic configuration of the board is:
 *
 * - Temperature Sensors pins: 23,24,25,26 and sensor 5 not using but connect to 19 
 * - Heater pins: 9,10,1,13 and heat 5 not using but connect to 14 
 * - LEDS: 22,2,12,11
 *   
 * (c) 2016 Juho Terrijarvi juho@miroculus.com, Miroculus Inc.
 * (c) 2014 Juanjo Tara j.tara@arduino.cc, Arduino Verkstad AB 
 * 
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
 *  You should have received a copy of the GNU General Public License
 *  along with this program.  If not, see <http://www.gnu.org/licenses/>.
 */


#include <PID_v1.h>
#include <math.h>


//Selector ping
#define SEL_1 46                 // Selector ping 1
#define SEL_2 47                 // Selector ping 2
#define SEL_3 48                 // Selector ping 3
#define SEL_4 49                 // Selector ping 4

//Temperature Sensors pin
#define TH_MIDDLEBED_1 A8                 // Temperature Sensor 2
#define TH_MIDDLEBED_2 A9                 // Temperature Sensor 3
#define TH_UPPERBED A10                   // Temperature Sensor 1
#define OPTIMAL_MIDDLE_TEMP 63
#define OPTIMAL_UPPER_TEMP 80
#define IDDLE_MIDDLE_TEMP 30
#define IDDLE_UPPER_TEMP 20
#define Threshold_temp 0.5
//Heater pins
#define HEAT_MIDDLE 2             // Heat 1
#define HEAT_UPPER 3            // Heat 2

//LED Sensors pin
#define PANEL_LED 22			        


// manufacturer data for episco NCP18XH103F03RB 10k thermistor
// simply delete this if you don't need it
// or use this idea to define your own thermistors
#define NCP18XH103F03RB 3380.0f,298.15f,10000.0f  // B,T0,R0


// STATES FOR STATE MACHINE
#define INIT      'I'
#define CANCEL       'C'
#define HEAT_BOARDS  'H'
#define INFO       'i'
#define SET_TEMP_UPPER 'U'
#define SET_TEMP_MIDDLE 'M'
#define READ_ASSAY 'R'


int MUL[6] = {
  A0,A1,A2,A3,A4,A5};				// Multiplexer  1



byte controlLPins[] = {
  B00000000, 
  B00000001,
  B00000010,
  B00000011,
  B00000100,
  B00000101,  
  B00000110,
  B00000111,
  B00001000,
  B00001001,
  B00001010,
  B00001011,
  B00001100,
  B00001101,
  B00001110,
  B00001111}; 


// holds incoming values from Multiplexer
int sensorValues[8][12] = {
};


//Define the aggressive and conservative Tuning Parameters
double aggKp=4, aggKi=0.4, aggKd=4; // d2
double consKp=1, consKi=0.05, consKd=0.25; //1, 0.25
double Setpoint;
//Define Variables we'll be connecting to PID's
double Input_MIDDLE, Output_MIDDLE, Setpoint_MIDDLE,Input_UPPER, Setpoint_UPPER, Output_UPPER,Input_MIDDLE_2;

//PID Controller for Heater
PID PID_MIDDLE(&Input_MIDDLE_2, &Output_MIDDLE, &Setpoint_MIDDLE, consKp, consKi, consKd, DIRECT);
PID PID_UPPER(&Input_UPPER, &Output_UPPER, &Setpoint_UPPER, consKp, consKi, consKd, DIRECT);


// enumerating 3 major temperature scales
enum {
  T_KELVIN=0,
  T_CELSIUS,
  T_FAHRENHEIT
};

byte states[] = {
  INIT, CANCEL, HEAT_BOARDS, INFO, SET_TEMP_UPPER, SET_TEMP_MIDDLE, READ_ASSAY};


// serial data
String inputString = "                         ";  // a string to hold incoming data
String parameters = "                         ";
String dataString = "                         ";
boolean stringComplete = false;  // whether the string is complete               
boolean LED=false;
boolean HEAT_ON = false;

int state = INIT;
char previous_state = INIT;
int defaultState = INIT;

void setup ()
{
  DDRL = DDRL | B00001111;  // this sets pins D3 to D7 as outputs

  // Temperature Sensors pin
  pinMode(TH_MIDDLEBED_1, INPUT);
  pinMode(TH_MIDDLEBED_2, INPUT);
  pinMode(TH_UPPERBED, INPUT);

  // Heater pins
  pinMode(HEAT_MIDDLE, OUTPUT);
  pinMode(HEAT_UPPER, OUTPUT);

  //Panel LEDS
  pinMode(PANEL_LED,OUTPUT);


  // Read temperature sensors
  ReaderSensorTemp();

  // Set degrees for PID algorithm
  Setpoint_MIDDLE = OPTIMAL_MIDDLE_TEMP;
  Setpoint_UPPER = OPTIMAL_UPPER_TEMP;

  // input string needs space
  inputString.reserve(30);  
  inputString = "";
  parameters = "";

  Serial.begin(9600);  // Begin the serial monitor at 9600bps
  Serial.println(F("Hope your day is nice and shiny!"));

}


void loop () {
    
  // print the string when a newline arrives:
  if (stringComplete) {
    // remove carriage returns and new lines
    inputString.replace("\n", "");
    inputString.replace("\r", "");
    Serial.println(inputString);
       
    // it there is anything to do with it, do it!
    if(isState(inputString[0])) {
      previous_state = state;
      state = inputString[0];
      parameters = inputString.substring(2);
    }
    // clear the string:

    inputString = "";
    stringComplete = false;
  }

  //Calculate PID for heaters
  if (HEAT_ON) Calculate_Heat();
  //Calculate_Heat();

  // state machine
  switch (state) {

  case INIT:
    previous_state = state;
    state = 'I';
    break;

  case CANCEL:

    HEAT_ON = false;

    Output_MIDDLE = 0;
    Output_UPPER = 0;
    computePIDs();
    
    Serial.println(F("Cancel$"));
    //delay(4000);

    //turn the PID's off
    PID_MIDDLE.SetMode(MANUAL);
    PID_UPPER.SetMode(MANUAL);
    
    //Setpoint_MIDDLE = IDDLE_MIDDLE_TEMP;    
    //Setpoint_UPPER = IDDLE_UPPER_TEMP;
    
    state = defaultState; 
    
    break;  

  case HEAT_BOARDS:  
    
    HEAT_ON = true;
      
    Serial.println(F("HEATING BOARDS$"));
  
    //turn the PID's on
    PID_MIDDLE.SetMode(AUTOMATIC);
    PID_UPPER.SetMode(AUTOMATIC);
    
    state = defaultState;
    break;

  case INFO:

    Serial.println(String(Output_MIDDLE) + "," + String(Output_UPPER) + "," + String(analogRead(TH_UPPERBED)) + "," + 
      String((analogRead(TH_MIDDLEBED_2))) + "," + 
      String(Temperature(TH_UPPERBED,T_CELSIUS,NCP18XH103F03RB,10000.0f)) + "," + String(Temperature(TH_MIDDLEBED_2,T_CELSIUS,NCP18XH103F03RB,10000.0f) * 0.6548 + 17.931) + "$");
    
    state = defaultState;

    break;

  case SET_TEMP_UPPER:

    Setpoint_UPPER = parameters.toInt();
    Serial.print(F("NEW UPPER TEMP:"));    
    Serial.print(Setpoint_UPPER);
    Serial.println("$");
        
    state = defaultState;
    break;

  case SET_TEMP_MIDDLE:

    Setpoint_MIDDLE = (parameters.toInt() - 17.931)/0.6548;  
    Serial.print(F("NEW MIDDLE TEMP:"));       
    Serial.print(Setpoint_MIDDLE * 0.6548 + 17.931);
    Serial.println("$");
        
    state = defaultState;

    break;
    
  case READ_ASSAY:
    
    Serial.print(F("READ ASSAY"));     
    Read_Assay();
    state = defaultState;
    break;

  } 
}

void setPin(int outputPin) {
  PORTL = controlLPins[outputPin];
}

void Read_Assay() {

  //set the PIDs to zero to boost LED power
  Output_MIDDLE = 0;
  Output_UPPER = 0;
  computePIDs();

  digitalWrite(22,HIGH);
  delay(500);
  
  
  //take 5 samples for measurement
  for (int j=0 ; j<5 ;j++)
  {
    for (int i = 0; i < 16; i++)
    {
      setPin(i); // choose an input pin
      ReadAssay(i);

    }    
    delay(1000);
  }


  digitalWrite(22,LOW);


  //Calculate the average of the measurements for each sample
  for (int k=0; k< 8;k++)
  {
    for (int l = 0;l < 12;l++)
    {
      sensorValues[k][l] /= 5;
    }
  }

  displayData();
  
  //Empty the array
  for (int k=0; k< 8;k++)
  {
    for (int l = 0;l < 12;l++)
    {
      sensorValues[k][l] = 0;
    }
  }
  
  //Empty possibly stored charge
  //take 5 samples for measurement
  for (int j=0 ; j<15 ;j++)
  {
    for (int i = 0; i < 16; i++)
    {
      setPin(i); // choose an input pin
      
      for (int k=0; k<5; k++) {
        
        ReadAssayEmpty(i);

      }
    }    
    delay(10);
  }  
}
void ReadAssayEmpty(int i) {

  for (int j = 0; j < 6; j++)
  {

    switch (i) {

    case 0:
      analogRead(MUL[j]);
      break;
    case 1:
      analogRead(MUL[j]);
      break;
    case 2:
      analogRead(MUL[j]);
      break;
    case 3:
      analogRead(MUL[j]);
      break;
    case 4:
      analogRead(MUL[j]);
      break;
    case 5:
      analogRead(MUL[j]);
      break;
    case 6:
      analogRead(MUL[j]);
      break;
    case 7:
      analogRead(MUL[j]);
      break;
    case 8:
      analogRead(MUL[j]);
      break;
    case 9:
      analogRead(MUL[j]);
      break;
    case 10:
      analogRead(MUL[j]);
      break;
    case 11:
      analogRead(MUL[j]);
      break;
    case 12:
      analogRead(MUL[j]);
      break;
    case 13:
      analogRead(MUL[j]);
      break;
    case 14:
      analogRead(MUL[j]);
      break;
    case 15:
      analogRead(MUL[j]);
      break;
    }
  }
}

void ReadAssay(int i) {

  //select the multiplexer
  for (int j = 0; j < 6; j++)
  {

    switch (i) {

    case 0:
      sensorValues[3][(j*2)+1]+= analogRead(MUL[j]);
      break;
    case 1:
      sensorValues[2][(j*2)+1]+= analogRead(MUL[j]);
      break;
    case 2:
      sensorValues[1][(j*2)+1]+= analogRead(MUL[j]);
      break;
    case 3:
      sensorValues[0][(j*2)+1]+= analogRead(MUL[j]);
      break;
    case 4:
      sensorValues[3][j*2]+= analogRead(MUL[j]);
      break;
    case 5:
      sensorValues[2][j*2]+= analogRead(MUL[j]);
      break;
    case 6:
      sensorValues[1][j*2]+= analogRead(MUL[j]);
      break;
    case 7:
      sensorValues[0][j*2]+= analogRead(MUL[j]);
      break;
    case 8:
      sensorValues[4][j*2]+= analogRead(MUL[j]);
      break;
    case 9:
      sensorValues[5][j*2]+= analogRead(MUL[j]);
      break;
    case 10:
      sensorValues[6][j*2]+= analogRead(MUL[j]);
      break;
    case 11:
      sensorValues[7][j*2]+= analogRead(MUL[j]);
      break;
    case 12:
      sensorValues[4][(j*2)+1]+= analogRead(MUL[j]);
      break;
    case 13:
      sensorValues[5][(j*2)+1]+= analogRead(MUL[j]);
      break;
    case 14:
      sensorValues[6][(j*2)+1]+= analogRead(MUL[j]);
      break;
    case 15:
      sensorValues[7][(j*2)+1]+= analogRead(MUL[j]);
      break;
    }

  }
}

// dumps captured data from array to serial monitor
void displayData() {
  Serial.println(F(""));

  int j=0;
  String str = "";

  for (j=0; j < 8; j++)
  {


    for (int i = 0; i < 12; i++)
    {
      str = str + sensorValues[j][i] + ",";
    }
  }
  Serial.print(str + "$");
  Serial.println(F(""));
  
}

void Calculate_Heat() {

  ReaderSensorTemp();
  SetTunings_PID();
  computePIDs();    


}    

void computePIDs() {

  PID_MIDDLE.Compute();
  PID_UPPER.Compute();

  analogWrite(HEAT_MIDDLE,Output_MIDDLE);
  analogWrite(HEAT_UPPER,Output_UPPER);
  /*
  
   analogWrite(HEAT_MIDDLE,0);
   analogWrite(HEAT_UPPER,0);
   */
}


void ReaderSensorTemp() {

  Input_UPPER = Temperature(TH_UPPERBED,T_CELSIUS,NCP18XH103F03RB,10000.0f);
  //Input_MIDDLE = Temperature(TH_MIDDLEBED_1,T_CELSIUS,NCP18XH103F03RB,10000.0f);
  Input_MIDDLE_2 = Temperature(TH_MIDDLEBED_2,T_CELSIUS,NCP18XH103F03RB,10000.0f);

}

void SetTunings_PID() {

  double gap1,gap2;

  gap1 = abs(Setpoint_MIDDLE - Temperature(TH_MIDDLEBED_2,T_CELSIUS,NCP18XH103F03RB,10000.0f)); //distance away from setpoint
  gap2 = abs(Setpoint_UPPER - Temperature(TH_UPPERBED,T_CELSIUS,NCP18XH103F03RB,10000.0f)); //distance away from setpoint


  if(Temperature(TH_MIDDLEBED_2,T_CELSIUS,NCP18XH103F03RB,10000.0f)>Setpoint_MIDDLE)
  {  //we're close to setpoint, use conservative tuning parameters
    PID_MIDDLE.SetTunings(consKp, consKi, consKd);
    Output_MIDDLE = 0;
  }
  else
  {
    //we're far from setpoint, use aggressive tuning parameters
    PID_MIDDLE.SetTunings(aggKp, aggKi, aggKd);
  }

  if(Setpoint_UPPER<Temperature(TH_UPPERBED,T_CELSIUS,NCP18XH103F03RB,10000.0f))
  {  //we're close to setpoint, use conservative tuning parameters
    PID_UPPER.SetTunings(consKp, consKi, consKd);
    Output_UPPER = 0;
  }
  else
  {
    //we're far from setpoint, use aggressive tuning parameters
    PID_UPPER.SetTunings(aggKp, aggKi, aggKd);
  }
}
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

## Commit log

2016-02-05 previous shield
    [MirOculousShieldv2.brd, MirOculousShieldv2.drl, MirOculousShieldv2.ods, MirOculousShieldv2.sch]
2016-02-12 3d files
    [2.5,3.5,1.stl, 6,3,1.5mm_final.stl, 6,3,5mm.stl, base.stl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]
2016-03-15 Create publishable version
    [2.5,3.5,1.stl, 6,3,1.5mm_final.stl, 6,3,5mm.stl, MirOculousShieldv2.brd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]
2016-03-22 PCB modification, CERN license
    [LED_003.GBL, LED_003.GBO, LED_003.GBS, LED_003.GTL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]
2016-04-08 Updated PCB print details
2019-04-06 Updated branch
    [LED_004.xlsx, SHIELD_007.xlsx, base.stl, cover.stl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]
2020-03-28 Deleted ATX, Added new board to board connectors and a possilibity to add a fan
    [LED_004.GBL, LED_004.GBO, LED_004.GBS, LED_004.GTL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]
2020-03-29 few corrections
    [SHIELD_008.xlsx, sensor_003.GBL, sensor_003.GBS, sensor_003.GTL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]

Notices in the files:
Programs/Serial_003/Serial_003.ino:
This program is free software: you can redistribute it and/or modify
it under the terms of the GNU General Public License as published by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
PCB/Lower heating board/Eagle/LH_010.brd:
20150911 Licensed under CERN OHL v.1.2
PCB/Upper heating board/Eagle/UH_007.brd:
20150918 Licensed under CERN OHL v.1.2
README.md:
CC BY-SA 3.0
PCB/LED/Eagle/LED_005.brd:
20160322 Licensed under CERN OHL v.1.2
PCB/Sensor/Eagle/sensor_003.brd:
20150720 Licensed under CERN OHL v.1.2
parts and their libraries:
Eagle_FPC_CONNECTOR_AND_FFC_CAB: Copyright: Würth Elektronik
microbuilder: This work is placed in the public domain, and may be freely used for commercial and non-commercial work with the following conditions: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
